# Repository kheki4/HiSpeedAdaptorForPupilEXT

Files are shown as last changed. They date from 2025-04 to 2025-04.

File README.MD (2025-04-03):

# Repurposing an SMI HiSpeed tower-mounted eye-tracker to be used with PupilEXT open-source pupillometry software

***

As SensoMotoric Instruments GmbH was acquired by Apple Inc. in 2017, and support has been discontinued for their products, the previous users of their devices started to encounter problems with their devices, but noone left to help them. 

If you happen to be a researcher with a faulty SMI HiSpeed system, which is serving as a several thousand euro worth piece of paperweight at the moment, you might want to consider turning it into at least a working pupillometer device. It is possible to repurpose this tower mounted eye-tracker by replacing its camera and switching to use the open-source PupilEXT software for pupillometry! 

Here I assume though, that that the IR illumination of your system is intact.
The transformation is fully reversible (if you keep the original SMI-installed Windows on original SSD of the SMI host PC).

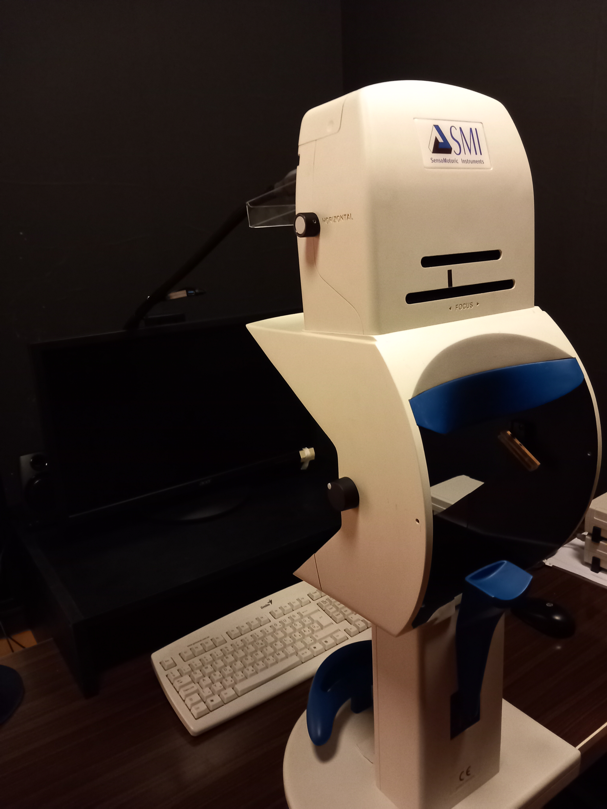
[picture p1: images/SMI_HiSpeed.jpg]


***

## Before you go with it

### There is an alternative

Importantly, Gaze Intelligence is another company formed by some of former SMI employees, who offer solutions to replace the old SMI devices, while keeping software integration compatibility. If anyone is interested, feel free to check them out first: https://gazeintelligence.com/

### Note on repairability of the built-in illuminator driver circuit 

The original SMI near-infrared (NIR) illumination driver circuitry is a very nicely repairable part of the system, so if you happen to have a problem with that, and have any interested electrics engineer student or any friend playing with DIY electronics, there is no need to worry. Accordingly, the repair details are not mentioned in detail here.

If you specifically have any problem with the NIR lighting, here below is a little help to find replacement parts for the driver circuit. The LED blocks are unlikely to malfunction, but can be repaired also, or swapped if only one block needs to stay operational. In case you wish to repair the driver circuitry, it is important you DO NOT CHANGE the state of the two blue square-shaped potentiometers on the printed-circuit-board, as they are for setting the brightness of the illuminators, and were factory-set to comply the EN 62471 eye-safety standard.

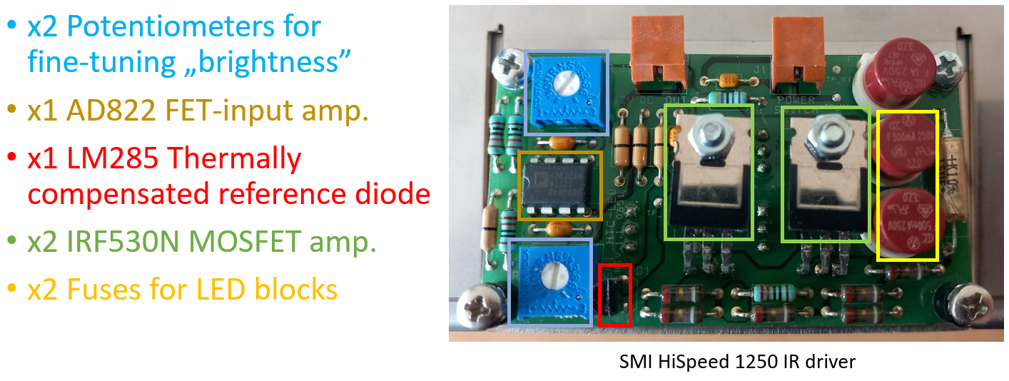
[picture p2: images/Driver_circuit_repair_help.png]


### Note on ethical and eye-safety compliance

The device after modification will not hurt the participants, or pose any threat to their comfort or health. Also, it should not affect EEG-compatibility, and as we have tested it already (using an USB3 interface camera), the modifications described below will not induce any electrophysiological recording noise in EEG, EMG or ECG recordings parallelly used with the system powered on. With the mentioned hardware modification of the HiSpeed tower mount, we change absolutely nothing with regard to the illuminator circuitry, which means that we do not introduce any change in the near-infrared illumination exposure to the participants' eyes, we only use the illuminators as they were produced in the SMI factory originally.

If you are to conduct research using the modified device, and you need to state the ethical compliance of the setup, you can just insert the following amendment text into your old/existing ethical approval application:
```
The eye movement activity of participants will be recorded during the experiment in a non-invasive manner, using an open-source system, which employs a camera manufactured by Basler (Basler AG, Ahrensburg, Germany), and the open-source PupilEXT software (B. Zandi, M. Lode, A. Herzog, G. Sakas, and T. Q. Khanh, “PupilEXT: Flexible Open-Source Platform for High-Resolution Pupillometry in Vision Research,” Front. Neurosci., vol. 15, Jun. 2021, doi: 10.3389/fnins.2021.676220).
The camera of the PupilEXT system is connected to the data recording computer via a safely sealed, electrically grounded cable, that it does not emit electromagnetic radiation to interfere with the operation of any other scientific appliance in the laboratory room. The camera is safely mounted inside a tower chin-rest structure, which is part of an older eye-tracker system from the manufacturer SMI (SensoMotoric Instruments GmbH, Teltow, Germany). The original camera unit from this SMI system was replaced by the aforementioned camera, to repurpose the device for use with the PupilEXT software. Importantly, the presence of this camera, and the powered state of this device does not cause any undesired electromagnetic interference with regard to pacemakers or human participants of the experiments. The camera does not emit light or near-infrared (NIR) radiation itself, but it uses the NIR illuminator units of the older SMI-system to ensure controlled lighting conditions for capturing monochromatic images of the eyes of the participants. This invisible light does not pose any threat to the heatlth of the participants.
```

And in case you are making image recordings of the eyes of the participants with the PupilEXT software, please add the following customisable text amendment to your "Declaration of informed consent" form that your participants always fill out:
```
I give my consent for the aforementioned party to record and store monochromatic images of my eyes, captured using an infrared video camera, to the aim of measuring my eye movement activity as part of this research. These images will be stored in an anonomized manner on protected computers for academic research purposes, and would be deleted whenever I choose withdraw my consent, now or anytime in the future.
```

At the same time, this instruction here is just a helping guide. All responsibility for your research will be yours for properly setting up and using these devices.

***

## Preparation

### What you will need

- Basler Ace or Ace 2 camera (Also described below)
- Compatible cable to connect your new camera to the PupilEXT host computer. If you are considering a high camera-to-computer distance, an active cable (i.e. power-supply-backed one) might be necessary
- Compatible lens with the chosen camera (Also described below)
- Screwdriver set with hex head bits
- 3D printed adapter part matching either the Ace or the Ace 2 camera mounting hole positions. (Strictly SLS-printed, not FDM. Also described below)
- Modeling superglue (e.g. 2g portion) 
- M3 hex nuts, 2 pcs (e.g. ISO 4032)
- M3x10 or M3x12, countersunk screws, 2 pcs (e.g. ISO 10642)
- M3x6 socket head cap screw, 3 pcs (e.g. ISO 4762)
- SSD to install a newer operating system on, which is supported by PupilEXT (optional, but recommended). Or as an alternate option, you can use a completely separate computer

### Obtaining PupilEXT

See the official software version at https://github.com/openPupil/Open-PupilEXT, or for an Experimental-Community-Version please also see the specific branch of the repository, or for its development version, see the GitHub fork here: https://github.com/sasfog/Open-PupilEXT.

*Important: to receive trial increments and messages to mark trigger timestamps and use several other features that might come handy for psychophysiology experiments, you need to install an Experimental-Community-Version release of the PupilEXT software.*

### Choosing the camera

You will need an industrial camera, which is (at the moment of writing this article) from the manufacturer Basler, compatible with the PupilEXT software. Recommended to choose a GigE interface version if the distance of the tower unit and the PupilEXT data recording computer is in 5 m or more of cable length. If less, you can use the USB3 vision interfaced cameras from Basler - however in this case it might be needed to also add an active (i.e. power-supply backed) cable to connect the host PC to the camera inside the tower unit, as USB cables have higher loss on supplied power to the camera. E.g. recommended is the Basler Ace aca2040-200um/gm, or Basler aca2040-90um/gm or aca1300-200um/gm or the Basler a2a1920-160um/gm.

Note that if you choose a GigE vision camera, you will occupy the single Ethernet port of the PupilEXT computer. So in order to be able to receive trigger timestamps (only available in the Experimental-Community-Version releases of the PupilEXT software)

Also note that if you use an USB3 cable to connect the camera to the data recording computer, the USB3 controller adaptor inside the computer probably (unlikely, but rarely) be too slow or provides insufficient power to the camera to function properly. If this is the case, you need to also obtain any other USB3 extension card to your PC (e.g. any Delock branded one will do) and plug that in, to connect the camera.

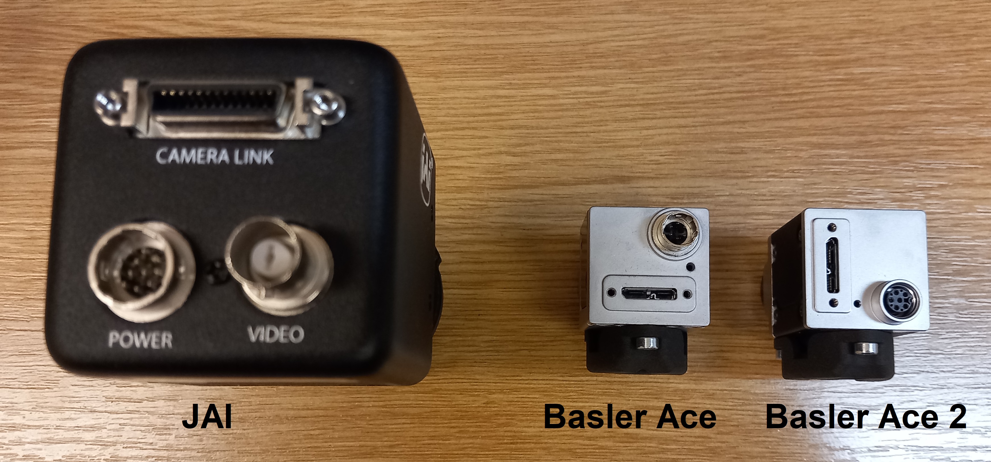
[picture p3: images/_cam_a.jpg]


### Choosing the lens

The stock lens that came with the SMI HiSpeed system is likely a Tamron one with a pre-set focal length, and with focus left adjustable.
Be sure to choose a kind of lens that does not have a near-infrared(NIR)-blocking coating on its glass. You do not necessarily have to buy NIR-specialized lens, as they are likely very pricey and have mostly advancements in reduced vignetting, lens distortion or chromatic aberration, but as we are operating in a narrow spectral range of illumination here, and the pupil of the participant will likely stay in the middle part of the image throughout the eye recording, it is safe to go with any lens that does not bother the 850-1000 nm spectral range of light.

You will need compatible machine vision lens, that fit the Basler camera you chose. It likely should be a C-mount lens. Optimal focal distance will depend on the actual camera you buy. The stock camera lens that you can dismount from the JAI camera of the SMI system will perhaps work with your Basler camera, but it will likely be suboptimal regarding its focal length or other properties.
On Ebay you can easily find even used good quality machine vision lenses, often marketed as "TV lens" from good manufacturers like: Edmund Optics, Ricoh, Fujinon, Kowa, Computar, Tamron, VS Technology, Pentax. Cheap knockoff lenses marketed unbranded or noname, will also often work well, only probably lens distortion would be slightly higher.

As NIR filter, you can either just unscrew the NIR filter that was in the original JAI camera of the SMI HiSpeed system, behind the lens, unside the camera housing. It is a C-mount intermittent lens, that needs to be unscrewed using a tweezer or a rectangular piece of metal sized ~24 mm on one side, then can be screwed into your new Basler camera, to lay between the lens and the sensor. Or you can just buy a filter that fits the filter thread diameter of your chosen lens. If you seek to buy lens, Schneider-Kreuznach (EU) or MidOpt (US) are research-grade quality producers of optical filters, but even cheap Ebay, Amazon or Aliexpress finds can sometimes be surprisingly good, pick as you wish. Be sure to choose a long-pass/IR-pass filter with cut-on wavelength of anything between circa 680 and 870 nm, likely 720 or 850 is the easiest to find.

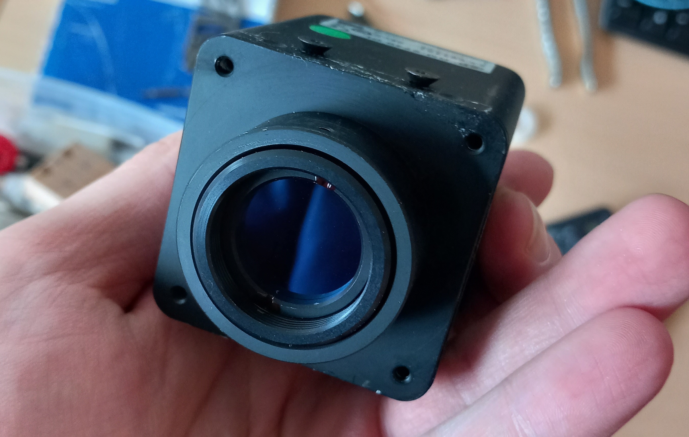
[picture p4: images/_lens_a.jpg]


The focus of your chosen lens will probably need to be adjusted sometimes. This is slightly inconvenient, as the lens you use likely has a focus setting ring at a different location than where the original SMI lens had their one. So you cannot just use the tuner knob anymore, but anytime you want to change focus, you will need to quickly take town the lid of the tower mount, and tune focus, and then put the lid back on. However, this maneuver might only be necessary for a few exceptional subjects as the tower mount itself acts as a good chin rest and if the cheek and forehead of the participant are touching its surface, likely the same focus is applicable to almost everyone. Importantly, you can broaden the depth of field by lowering the aperture (setting the F number higher) on the lens. This is what you need to take care of. Be sure to place back the lid on the unit once you are all set, to prevent the participant from accidentally touching it (altough all touchable metal parts are grounded, so there is practically zero chance of electric shock for them).
If you happen to have your focus ring surprisingly at the same location where the slits of the tower head unit lid are located by chance, you can consider using lens ring lock screw extender, or just buy a longer screw and you can make your life easier. Typical lens ring locking screws are just regular knurled metric screws with one of the following thread sizes: M1.2, M1.4, M1.6, or M2. The exact type you need to find out by measuring this on your existing lens screws or consulting the lens documentation.

If you do not know what lens to choose, and cannot find anyone to help choosing the right lens, you can just choose to buy a variable focal length lens (varifocal lens, or "zoom" lens). But note that these usually have a limited F-value setting, so the image brightness vs. depth-of-field tradeoff would have to be considered: ultimately the image would be a little darker and slightly noisier, or it will be slightly harder to keep the pupil in focus when participants move.

### For example

In our lab we use a Basler a2a1920-160umBAS camera, with 12-36 mm varifocal lens, constantly set to 36 mm now, and f/4 aperture, and equipped with a 720 nm cut-on wavelength filter. In PupilEXT (Experimental-Community-Version release) we currently use the camera with 2x binning, and at 50 FPS to record images. Exposure is 10000 µs and analog gain of 15 dB. With the mentioned settings it produces the following image:

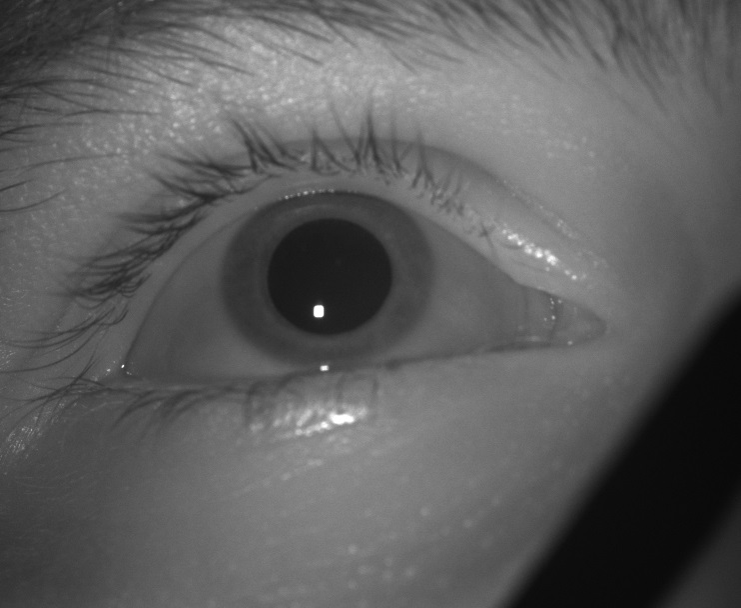
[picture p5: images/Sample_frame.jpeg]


### The 3D printable adapter

You need an adapter element that will make your selected Basler camera fit in the tower assembly, particularly inside the machined aluminium cage inside the tower head unit. The old JAI camera was quite big (50.8x50.8 mm), but the Basler cameras will be smaller (29x29 mm). Also, the mounting hole positions differ, as the JAI one was mounted with two screws, but Baslers employ 3, in a different constellation.

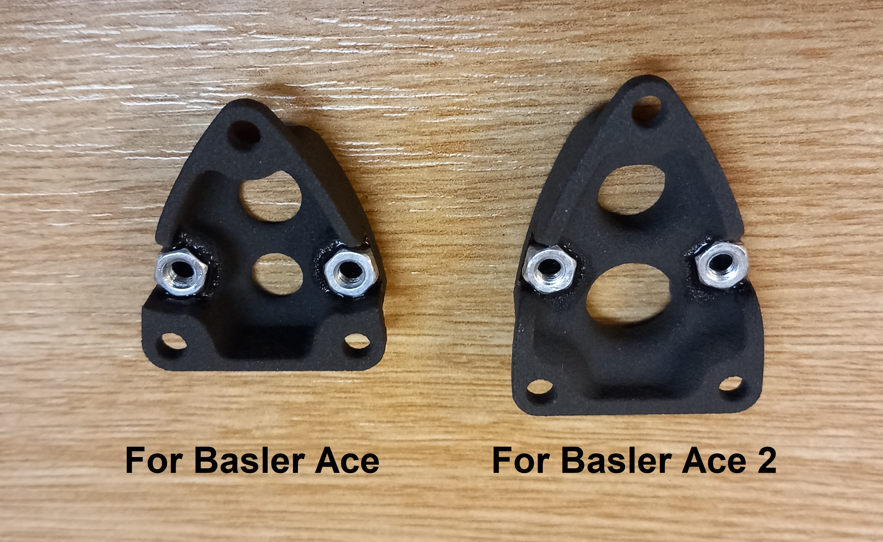
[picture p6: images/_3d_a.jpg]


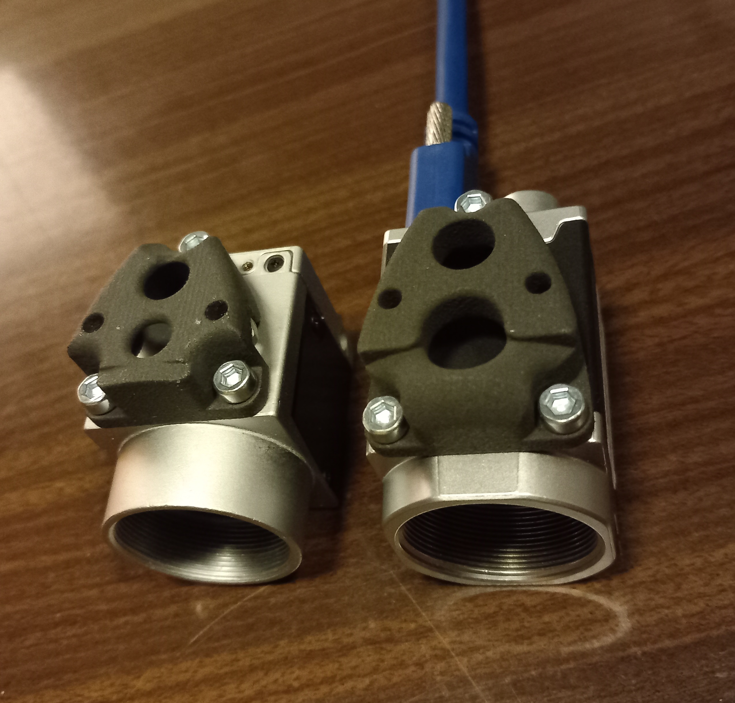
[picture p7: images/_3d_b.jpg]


*You can find the SLS 3D-printable parts modeled here in this repository.*   

[For Basler Ace series cameras](https://raw.githubusercontent.com/kheki4/HiSpeedAdaptorForPupilEXT/master/SMI_HiSpeed_Basler_ace_adaptor_n.stl)

[For Basler Ace 2 series cameras](https://raw.githubusercontent.com/kheki4/HiSpeedAdaptorForPupilEXT/master/SMI_HiSpeed_Basler_ace2_adaptor_n.stl)

Choose the one you need, either for Basler Ace or Ace 2 (or any other cameras of Basler, given it fits the same 3 mouting holes). Once printed, adding two M3 hex nuts and gluing them with a little amount of super glue, will be necessary to mount your new camera with the adapter into the SMI tower unit.

Specifically SLS-printing of the 3D part is necessary, beacuse as the camera can get very hot during use, an FDM-printed camera holder could deform in the heat.

Even though less widespread than FDM, SLS-printing is super easy and cheap in this size and quantitiy. I recommend either JLCPCB or PCBWay, but other companies also exist all around the globe, that support printing a little part like what we need, for likely around 1-2 USD (as of 2025, plus VAT and shipping).

At JLCPCB or PCBWay, you can just upload the needed .STL file to the online inquiry page, select SLS as printing method with any basic SLS material, and place the order! It is that easy, 5 minutes.

## Instructions

After you obtained all necessary components, to repurpose your system for use with PupilEXT, you need to follow these instructions:

1, Install PupilEXT on any compatible computer with a supported operating system, according to the walkthrough available on its GitHub page. You can use any computer you wish, but given you have the SMI host PC of the dead SMI HiSpeed system, it is logical to just try installing PupilEXT on it. This tutorial assumes that you go that way. But (at the moment of writing this article) PupilEXT does not have support for 32bit operating systems, so you cannot just install it on the stock SMI host PC. So, you need to either:  
- equip your former SMI host PC with a new SSD and install a PupilEXT compatible platform OS onto it (Windows 7 x64 recommended, but Linux or Mac is also possible), or   
- you can also just rewrite the factory-included SSD containing Windows 7 x86 with an x64 version as a new installation, although it might still be useful sometime, if you keep the original SMI installed system on it untouched, so the former option is recommended. 

2, In the observer room, unplug the CameraLink cable from the PC that goes to the HiSpeed tower mount in the experiment room, as it will no longer be needed. But keep the 12 v power supply attached, as it is needed to feed the IR illuminator of the tower mount unit. Pull out only the power cord of the power supply, for the duration of this tutorial.

3, In the experiment room, we will now partly disassemble the tower mount unit. Be sure to remove the dichroic "hot" mirror from the assembly first, by sliding it upwards. This mirror is used to reflect the invisible ~910-940 nm NIR light from the illuminator to the head of the participant and project the image of the eyes back to the camera. A mirror like this one is extremely hard to obtain and very expensive, so handle it with utmost care.

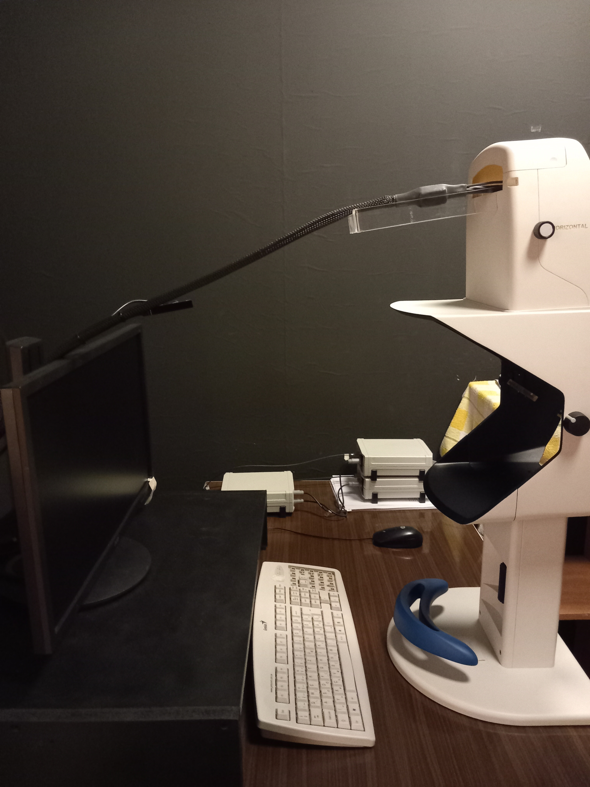
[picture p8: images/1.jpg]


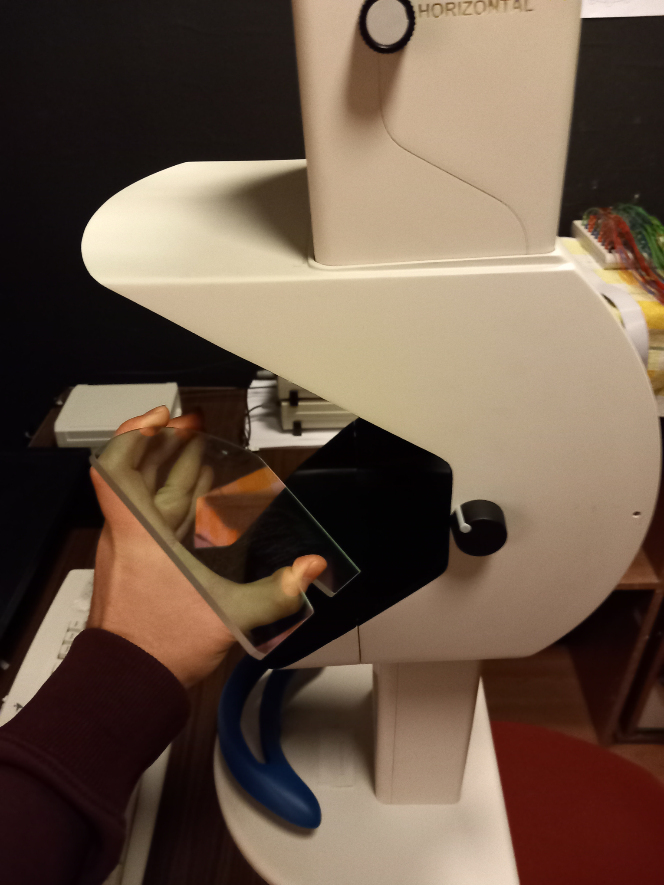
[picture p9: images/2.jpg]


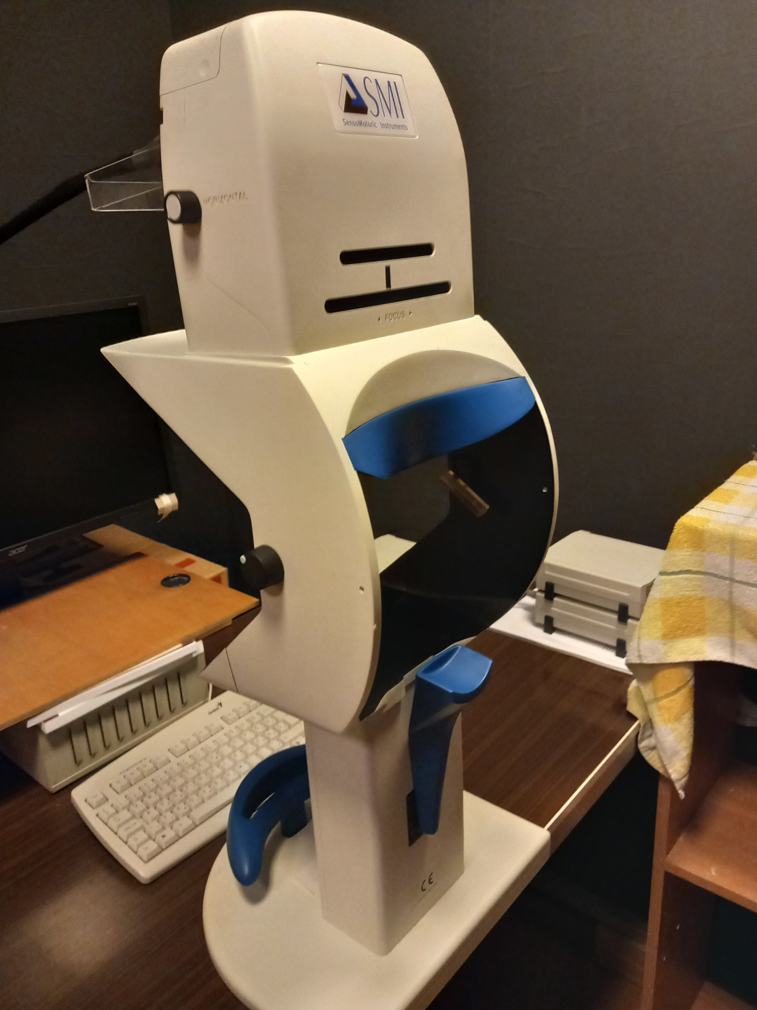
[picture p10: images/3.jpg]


4, The structure of the tower mount is MJF-printed plastic, which is surprisingly flexible, but please try to handle it softly to avoid any cracks.
Lift up the smaller lid of the tower head enclosure, facing the cables/monitor, which will just snap out easily.
Now remove the larger lid on the tower head enclosure (the one that has a nice SMI sticker on it from the side of the participant), by tilting it and pulling gently to the direction opposite of the experiment PC monitor. It should easily snap out, then you can lift it in a tilted position to remove from the tower assembly.

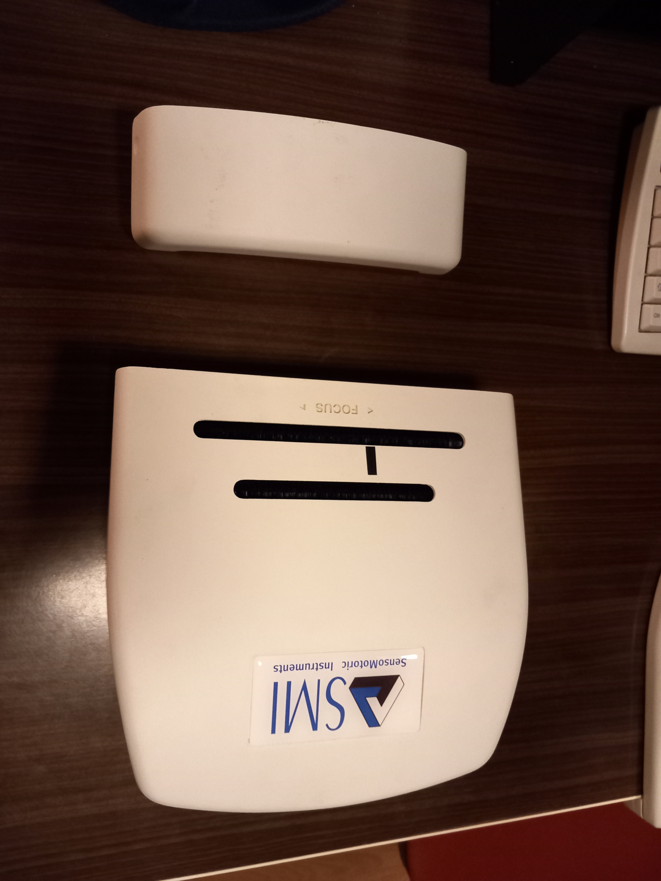
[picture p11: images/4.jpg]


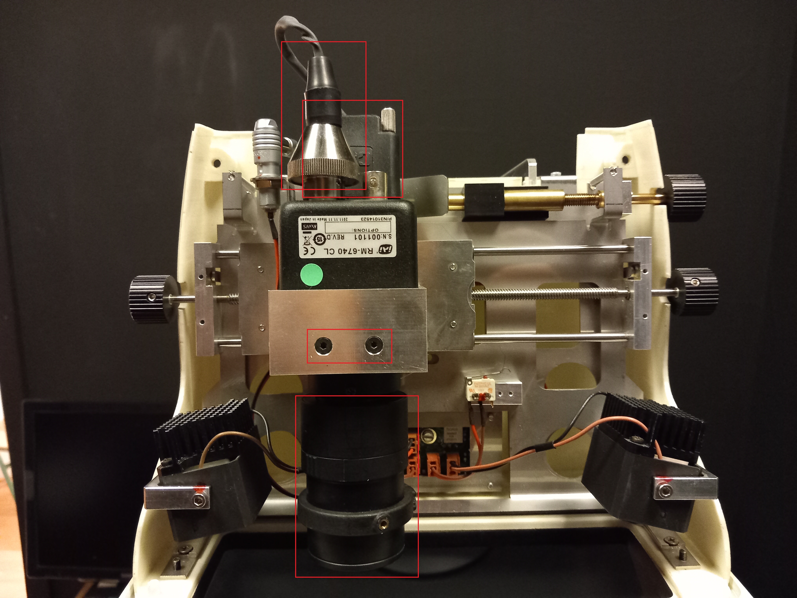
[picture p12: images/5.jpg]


5, Now we will remove the old JAI RM-6740CL camera of the SMI system.
You need to remove the CameraLink cable, by unscrewing its two little screws and pulling its end from the camera. Also please unplug the 12pin HiRose (mushroom-like looking) connector that feeds the camera with 12 v power. The connector only needs to be pulled, not rotated. The other end of the HiRose cable could also be disconnected from the IR power board, but it is not easy to access without further disassembling the structure, so you can just leave the end of the connector hanging there freely, without jamming any of the mechanical parts of the camera angle adjustment assembly of the tower head.
Do not unplug the 90 deg 4 pin connector that supplies 12 v power to the entire tower head unit (marked with "12 v" sticker), as this is needed later to feed the illuminator driver circuit.
Unscrew the lens from the camera, and remove the focus setter extender pin/knob/screw from its side if necessary.
Now unscrew the two black socket head countersunk M3 screws that hold the camera in its aluminium cage (these screws cannot later be used to screw in our new camera, as they would be too short). Now you can remove the camera by sliding it upwards, out of its cage.

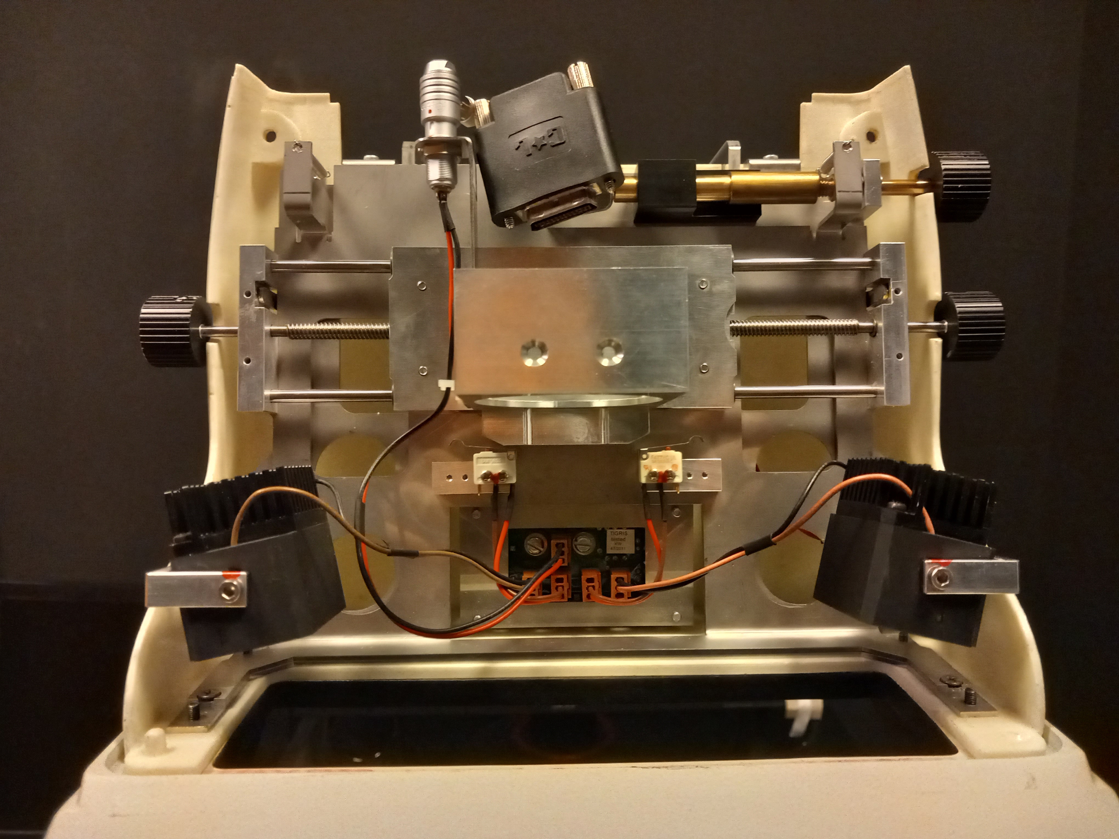
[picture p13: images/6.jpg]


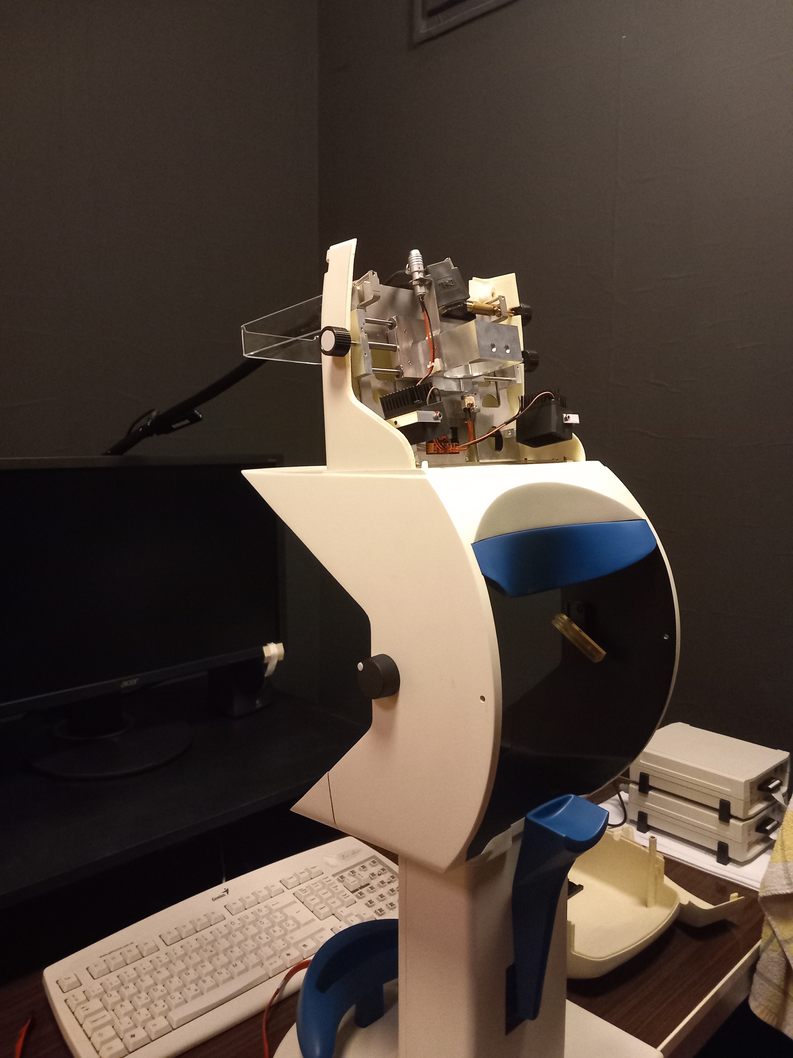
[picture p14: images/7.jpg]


6, Now we prepare the camera to be assembled into the tower mount. First fit the two M3 nuts into the 3D-printed adapter part, if you have not done already. The location of the nuts is shown below.



7, Now screw the camera onto the 3D-printed adapter part, using the three socket head cap M3 screws with 6 mm length. Now screw the camera into the aluminium cage inside the tower head unit, using the two countersunk M3 screws that you have, driving it through the cage, and the adapter, to screw them into the two hex nuts that are on the inside of the adapter part.

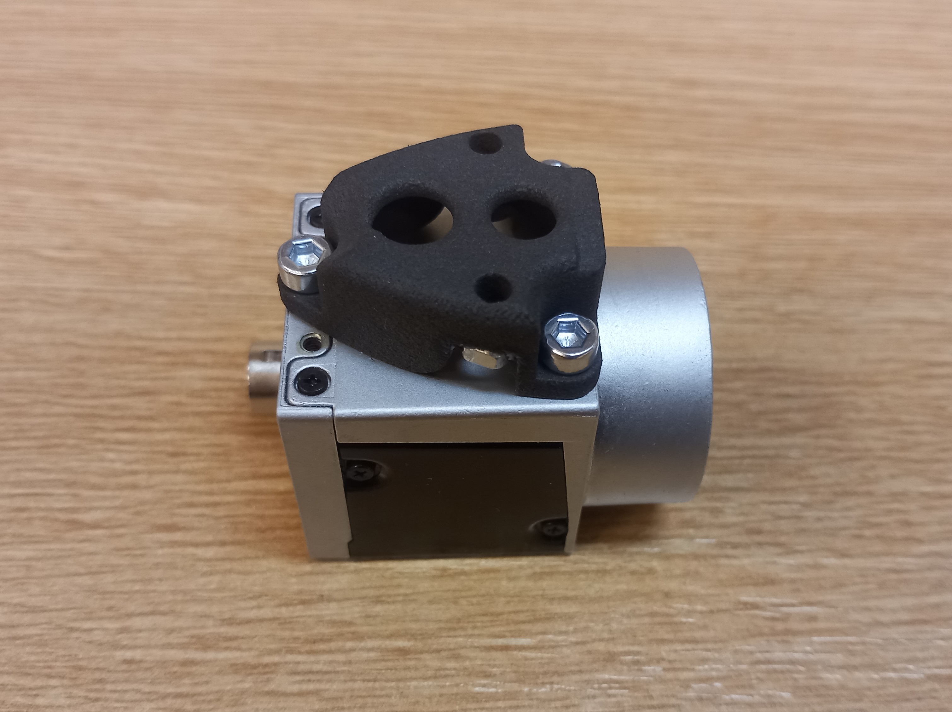
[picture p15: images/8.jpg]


8, Screw the lens into the camera. If you have a filter to be screwed onto the lens, fit that as well.

9, Screw in the USB3 port or alternatively/depending on your camera model, insert the Ethernet cable to the GigE port of your camera, and connect it with the host PC that has the PupilEXT software installed. 

The example pictures below show a Basler Ace series camera (top two; Basler aca1300-200um) and a Basler Ace 2 series camera (bottom two; Basler a2A1920-160umBAS) mounted into the tower assembly.

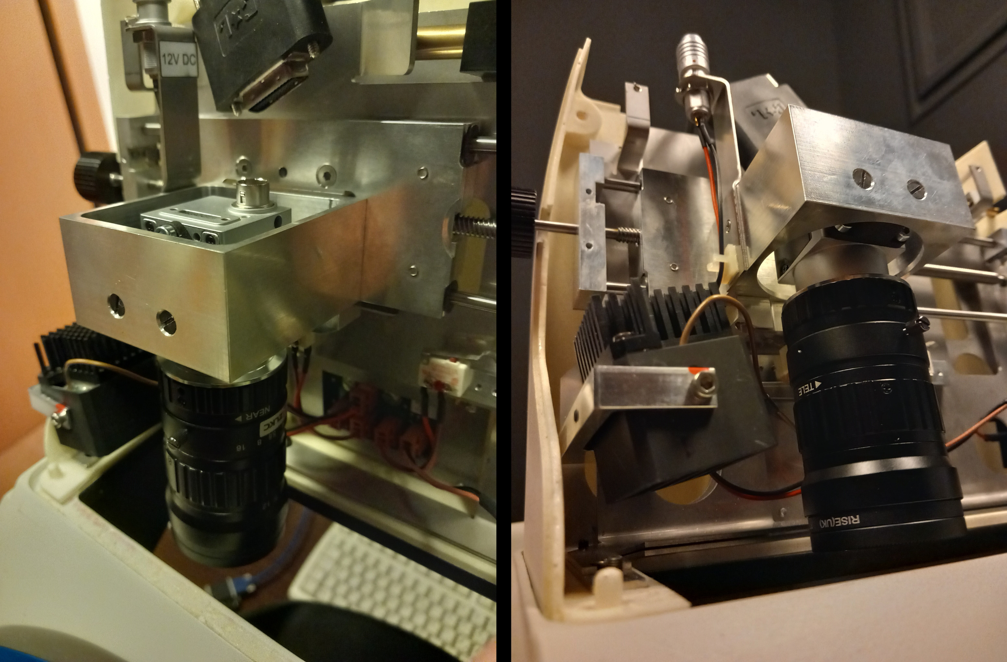
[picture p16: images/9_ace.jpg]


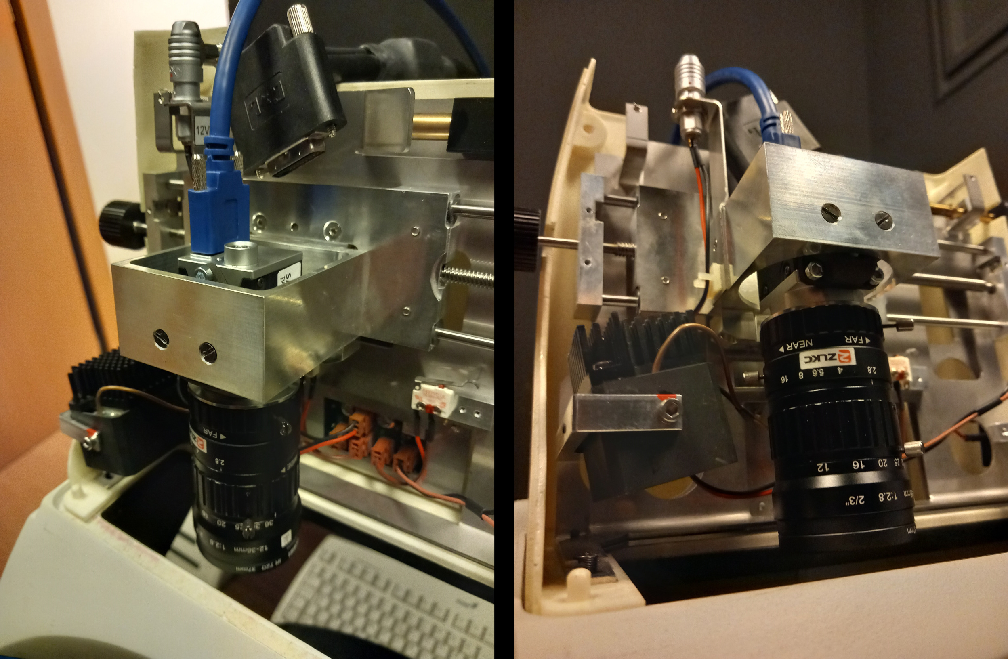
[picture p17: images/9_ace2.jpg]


10, Now place back the bigger lid and the smaller lid into the tower mount assembly to cover the cables and ensure that unwanted light from the ceiling of the experimental room will not be reflected to the face of the participant from the dichroic mirror by chance. 

11, Carefully place back the dichroic mirror to the tower mount structure. Be sure to fit it with the correct side facing the participant's face (its first-mirror surface, which is marked by a tiny triangluar chamfer on the bottom left side of the mirror, matching a tiny triangular notch on the left bottom of the transparent holder slides).

12, Replug the power supply of the system to mains in the observer room. Now you are free to switch on the IR light of the tower mount unit, and open the Basler camera with PupilEXT to make recordings of the pupil!

***

## Serving suggestion

The IR illumination of the SMI HiSpeed system is designed in a way that there are 2 light emitters inside the tower head. If the camera is in the middle position, all 2 illuminators will operate when the system is powered on. But if the camera is shifted to the right-eye or the left-eye, only the corresponding one illuminator will stay on. This kind of operation (i.e. only lighting and recording one eye) is highly recommended, as a single corneal reflection trace ("glint") of the illuminator will be much easier for the pupil-detection algorithm of PupilEXT to filter out, than 2 traces. Moreover, if just one eye is recorded, the pupil can be kept in the center of the camera image easily, which reduces pupil data artefacts originating from mainly uneven lighting, vignetting and lens distortion. You can adjust the camera to the left or right using the adjustment knob on the outside of the tower head. 

Of course, once you are using the image of one eye only, it is beneficial to choose a lens that allows a zoomed-in view of one eye. If you chose a varifocal lens, this just means to set the focal distance to your liking and lock it there. 
Importantly, one possible downside of using a varifocal lens is that, once its focal distance ("zoom") is changed, the size of the pupil will go with it, and also the quantization error of the real vs. image-captured pupil. So at least a dummy-eye recalibration or other control is needed for these changes, as well as a new lens calibration if you use that feature in PupilEXT. Still it is completely okay to use a varifocal lens, if you are sure that you will not change the zoom between experimental conditions, or participants. Below you can see the difference in a binocular and monocular constellation.

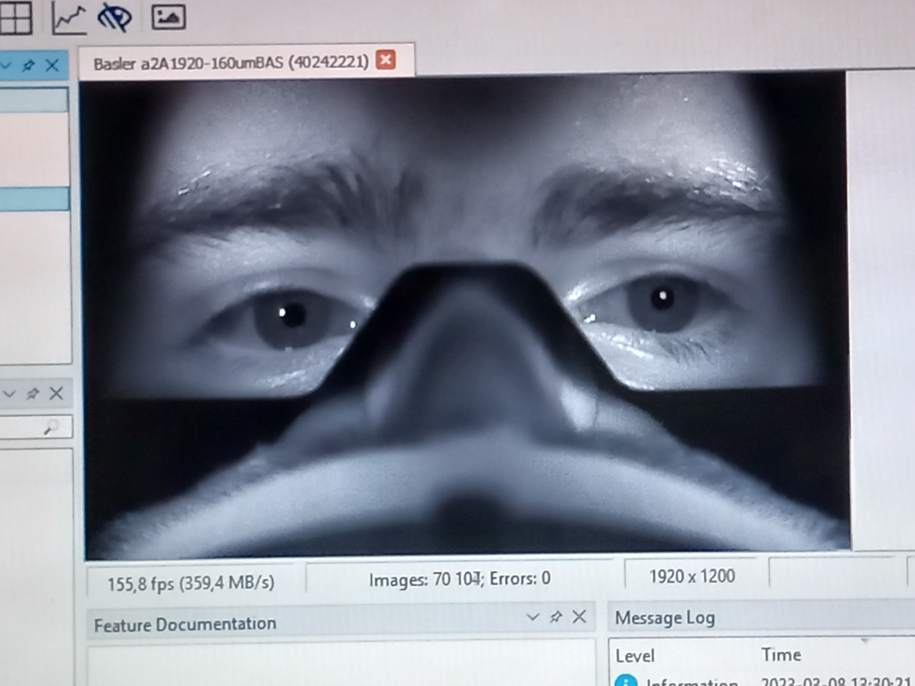
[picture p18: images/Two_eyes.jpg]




***

## Additional note

Author: Gábor Bényei @ BUTE

License: CC BY-NC-SA

The 3D-printable models used here were created with Autodesk Inventor 2024. The models and any derivative work should be used for non-commercial, research/education purposes only.

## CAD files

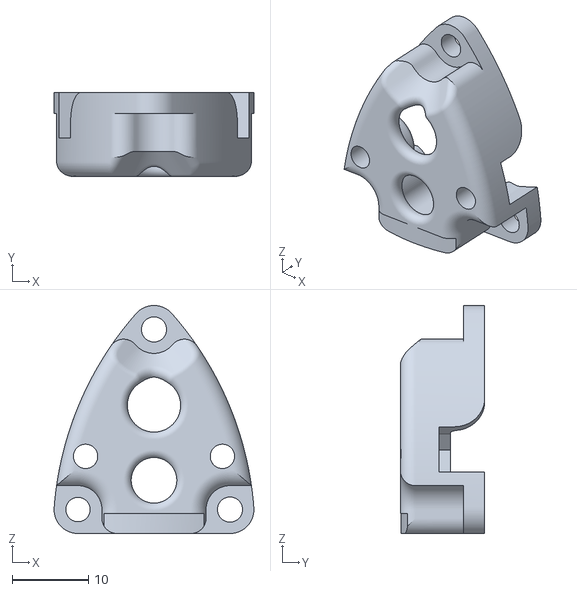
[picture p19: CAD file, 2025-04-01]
SMI_HiSpeed_Basler_ace_adaptor_n.stl
26.3 x 11.1 x 30.0

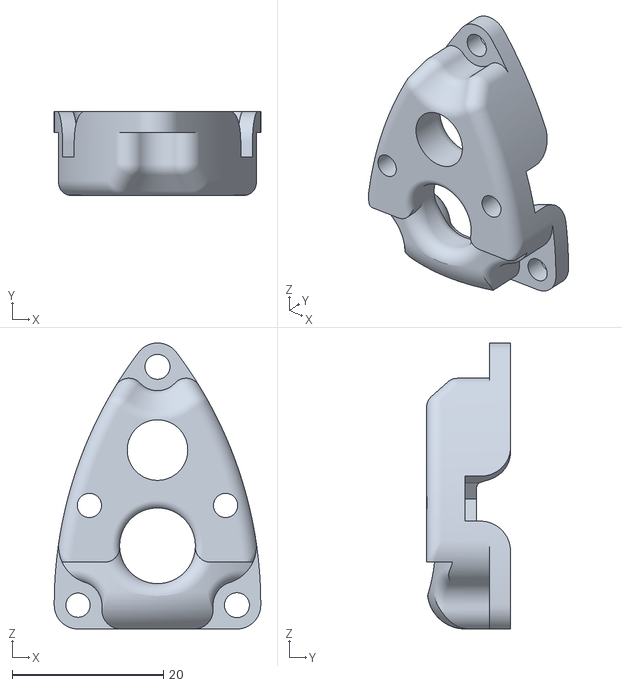
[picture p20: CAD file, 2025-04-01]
SMI_HiSpeed_Basler_ace2_adaptor_n.stl
27.3 x 11.1 x 37.8

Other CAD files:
editable_models/SMI_HiSpeed_Basler_ace2_adaptor.ipt
editable_models/SMI_HiSpeed_Basler_ace_adaptor.ipt
